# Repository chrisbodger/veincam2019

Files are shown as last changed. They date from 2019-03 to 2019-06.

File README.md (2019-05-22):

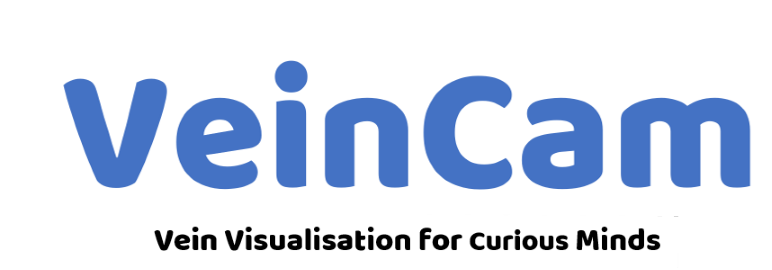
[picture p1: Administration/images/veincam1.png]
VeinCam


VeinCam is an educational tool for vein visualisation. It uses near infrared (nIR) light and a camera to stream a real-time image where veins can be easily seen. It is an open-source, build-it-yourself device so anyone who finds it useful will be able to construct it. There is a how-to guide of what materials to buy, how to put them together and the software to upload to get it all working.

This is the repository for the continuation of the VeinCam Project as an ANU Engineering Captone Project in 2019. The repository for the previous work can be found [HERE](https://www.github.com/chrisbodger/veincam). This repository will be used to delineate and document the progress made this semester, in what is to be the next chapter of this exciting project. 

---
# Table Of Contents
1. [Project Goals](#1-project-goals)
2. [Feedback](#2-feedback)
3. [Project Updates](#3-project-updates)
4. [Concept of Operations](#4-concept-of-operations)
5. [Meeting Minutes](#5-meeting-minutes)
6. [Decision Log](#6-decision-log)

---
# 1. Project Goals
There are 3 goals we wish to achieve this semester:

1. Develop a set of hardware requirements that are suitable for the VeinCam Project.
2. Optimise the software to run more efficiently.
3. Compile procurement options to develop kits to be able to be sold onto those who wish to build a VeinCam for themselves.

# 2. Feedback
A feedback form has been created for the interest of our stakeholders, should they wish to pass on any changes or improvements they believe to be prudent. The form can be found [here](https://goo.gl/forms/8cw5eWdaOY5C1jBo1).

# 3. Project Updates
### Week 11 - 22/05/2019

### Poster Showcase
The team presented VeinCam to a large science and engineering audience at the Project Showcase on the 20/5/19. A summary of the presentation and feedback is available [here](Administration/Communications/Poster-Presentation-Summary.md).

### School Visit
The team showcased VeinCam to Gungahlin College and gained insightful feedback into how VeinCam could be used in a secondary school environment. A summary of the visit is available [here](Administration/Communications/Gungahlin-College-Visit-210519.md).

#### Hardware
Final prototypes of the VeinCam enclosure completed, along with some PCB changes to better utilise onboard LEDs. Pricing for enclosure, along with final bill of materials determined. 

### Software

This week was spent getting all documenation up to date. Colour functionality added to MJPEG steam, fixed banding effects and scaling to better suit mobile and tablet users. 

### Previous Updates
More specific updates regarding each sub-team are available in the sub-team work diaries. These can be found in the [Hardware](/Hardware/HardwareDiary.md) and [Software](/Software/SoftwareDiary.md) folders, as well as team [Decision Logs](/Administration/Project/Decision-Log.md) are other locations for progress notes, should they not be located on this page.

# 4. Concept of Operations
Our Concept of Operations has been signed off by all parties involved. 

The [Concept of Operations](Administration/Project/CONOPS.md) document can be found in our repository.

# 5. Meeting Minutes
The team regularly meet to formally discuss the project's progress, as well as through other communication channels. the minutes from the formal discussions can be found in the [Meeting Minutes](Administration/meeting-minutes/) directory.

# 6. Decision Log
Major decisions that affect the majority or all of the project's future work and/or operations can be found in the [Decision Log](Administration/Project/Decision-Log.md/).

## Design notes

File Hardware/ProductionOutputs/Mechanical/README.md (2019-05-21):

## NOTE
We are relying on the draft angle from the laser cutter to hold the lens in. Different lasers/lenses/focal lengths will alter this draft angle and this needs to be taken into account.  

We also needed to flip the top acrylic to ensure that the lens would not fall out, as by default the lens was pushed in from the front. 

The dimensions may also need to be altered depending on how wide the laser cuts.

Any questions ask Josh, easier to explain with a VeinCam in hand and in person.

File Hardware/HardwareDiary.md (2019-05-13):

# Hardware Log

### Week Beginning 04/03/2019
* Looking into single board computers which would be suitable for the project.
	* Ideally smaller than a Raspberry Pi 3 B +, but more powerful than a RPi Zero.
	* RPi 3 A + was found as the only feaseable solution.
* Research into off the shelf cases which would suit above RPi 3 A + board, and required supporting hardware.

### Week Beginning 11/03/2019
* Rough design of possible case solutions, including extruded aluminium, COTS plastic enclosures, and custom cut acryllic.
	* Modeling of above designs in Fusion 360, including rough design of custom printed circuit assemblies to see mechanical fit.
* Preliminary schematic design for RPi 3A+ Hat to allow prelim BOM generation and costing.
* Preliminary schematic design for RPi Zero W Hat to allow prelim BOM generation and costing.
* BOM generation and component selection for both Hats.
* Estimated costing for both RPi Zero and RPi 3A+ devices, inclusive of PCA's and supporting hardware.

### Week Beginning 18/03/2019
* Created footprints and sourced / drew 3D models for all required components on PCA.
* Laid out RPiZero Hat, begun layout on RPi3A+ hat.
* Ordered parts from Mouser for new boards.
* Plans for RPi3A+ hat changed, no longer integrating charge circuit so changed schematic and laid out new design.
* Finished layout for both boards, got team approval, order placed 23/3/19 with JLCPCB. ETA Friday Week 5.

### Week Beginning 25/03/2019
* Extended discussions between Josh and Chris regarding possbile case designs going forward.
* Prelim case design for RPi3A+ completed. Awaiting boards for RPiZero before continuing with case design for the smaller platform. 
* General Makerspace + specific laser induction completed by Josh, will allow use of laser cutter to cut acrylic. 
* Shopping trip to purchase all required hardware for prototype build. 
* Test fitting and changes to mechanicals to account for differences in models vs actual.

### Week Beginning 1/04/2019
* Manufacturing of acrylic enclosure including updating lens mounting.
* Assembly of PCA's and testing, all appear to be functioning nominally. 

### Week Beginning 8/04/2019
* Laid out v2 of the VeinCam Zero to better fit a custom cut acrylic case instead of the official RPi case. 
* Begun design of v2 enclosure for the VeinCam Zero
* Changed VeinCam Plus enclosure to decrease size of IR acrylic required. 

### Week Beginning 15/04/2019
* Continued design of the v2 enclosure, and found it very hard to design around. 
* Through discussions with Ben and the team, have decided to scrap the zero due to the design challenges we will face wrt hardware, and the lack of performance which software is experiencing. 

### Week Beginning 22/04/2019
* Cut new case designs including IR acrylic for first time.
* Handed out to team members and Ben, awaiting feedback before continuing further. 
* DFM improvements to the VeinCam PCB

## Week Beginning 29/04/2019
* Resign of the enclosure to address issues with latest rev + shrink IR lens size. 

## Week Beginning 6/5/2019
* Laser cutting of revised case
* Assembly instructions written up

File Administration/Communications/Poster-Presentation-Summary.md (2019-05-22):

The Poster Presentation was held on the 20/5/19 in the Hannah Neumann building at ANU. VeinCam saw a strong number of people interested and participate in the presentation.
All members were present at various times during the presentation. Our stall had a VeinCam running to demonstrate on people's arms, a website on another touch-screen laptop for virtual representation and of course, our poster, which drew in the crowd and several people commented on its design and professionalism.
In particular, one university colleague of Alex stated that someone had come up to them and said they were "very impressed" with what the VeinCam team had achieved.

Matt from Questacon, a client for another Capstone project group, gave suggestions as to how VeinCam could potentially be upscaled to be made into an exhibit at the Q-Lab:
- A large high resolution camera with a large screen. The camera faces down, and patrons place their arm underneath.
- Signage could encourage blood flow in the way of exersice, such as 10 jumping jacks, to then see how that affects bloodflow in the arms.
- VeinCam kit could then be sold in the gift shop!
- A potential Capstone project for the following semester.

Other patrons pointed out to us that being a cheap, infrared camera, that it could be further developed to have several other uses:
- Night sight camera/cheap doorbell security option.
- Temperature/heat signatures at a low level (much cheaper than ones on the market currently).
- Assisting in household chores where detecting hot spots would be useful. 

Overall, the VeinCam team's presentation was a success and provided an engaging, interactive experience for its audience.

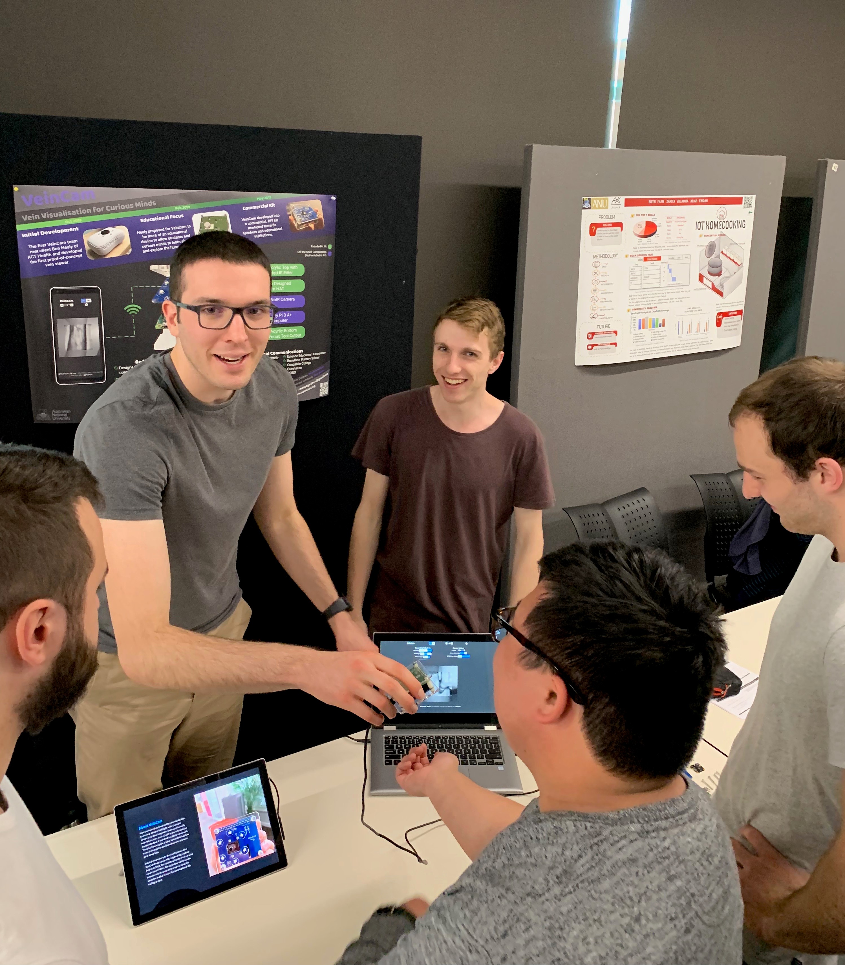
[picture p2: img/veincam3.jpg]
VeinCampres


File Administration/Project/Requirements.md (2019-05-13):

| Author        | Date Modified           | Version | Completion Status  |
| :-------------: |:-------------:| :-----:| :----:|
| Alexander Ollman   | 13/05/2019 | 2.0 | Completed for Audit 3 |

# System Requirements

| System Requirement  | Metric | Test | Validation | Client Importance (1 Lowest - 5 Highest) | Requirement Met? |
| :-------------: |:-------------:| :-------------:| :-------------: | :-----:| :----:|
| Compared to other devices with similar functionality, the produced device must be relatively inexpensive.  | Dollars, Australian | <$500AUD (Typical Public School Science Budget) | Cost of production VeinCam (minus packaging, freight, external costs) is less than $150 to consumer. | 3 | Yes, with reservation |
| The device must be simple to construct, easily reproduced (and/or easily manufacturable).  | Cost per unit | Cost per unit is <50% of total cost to consumer; contains mostly off-the-shelf components; can be manufactured with common machines, worldwide. | Cost per unit of is $13.49 for designed componentry, remainder of cost is from off-the-shelf components (Raspberry Pi A+, PiCam). Designs are open source and easily manufacutred with a laser cutter and PCB routing machine. | 5 | Yes, with reservation. |
| The device must be simple to use. Ease of use should be correlated with the intended educational application of the device, and as such be relevant for expected users. | Time, minutes | Time taken to assemble by unknown party, student. | Nursing student (Rachael Weigand) assembled VeinCam prototype closely resembling final design in 8 minutes (without camera focus adjustment, software setup). Device does not require further software setup and only knowing how to connect to a WiFi network is requied. | 2 | Yes, with reservation |
| The device must be able to use near infrared (NIR) illumination and real-time image processing to make veins appear most visible in an efficient manner. This criterion must be of a level of quality that is satisfactory for educational use. | #Infrared LED's | #Infrared LED's > 0, Veins Clearly Visible | There are six dual-wavelength (840nm and 950nm) infrared LED's which provide sufficient illumination on a subject and show clear, defined veins in the majority of test subjects (dependent on skin type, body fat) | 2 | Yes |
| The device must run primarily off of battery power. | Battery Capacity (mAh) | Battery Capacity > 0 mAh | The device contains no internal battery. However, the device is light and portable enough to be comfortably used with an external battery. | 1 | Yes, with reservation |
| The device must be able to wirelessly connect to an external device with a screen. | Wireless Connectivity Capability | - | Unit contains Built in WiFi + Bluetooth capability, connects to any external device with a screen and WiFi capability using WLAN connection | 4 | Yes |
| The device must be portable and mobile. | Weight, grams (g) | Total Net Weight < 200g | Unit is light (110g) and is easy and comfortable to hold in one hand. Device requires external power, which requires a cable connected to an external power source. This will commonly be either an exernal battery pack, a personal computer or an AC wall socket. | 4 | Yes, with reservation |
| The device must be reasonably easy to maintain, clean and fix in the event of failure/break/degradation. | Time, minutes | Time taken to be disassembled and reassembled by unknown party, student. | Device is completely modular and can be disassembled within 5 minutes, without the need for tools. Individual parts are easily accessible and two of the three major components are off-the-shelf. | 3 | Yes |
| The device should display veins in a wide variety of use-cases. | - | Veins clearly visible and defined on wide on differing external parties (e.g. dark-skinned, tattooed, hairy) | The device has not been tested outside of the testing confines of the project in accordance with ANU Ethics guidelines. Within our own testing, we have verified veins are clear and visible on a limited yet varied user sample size. | 5 | Untested, with reservation |
| The device is manufacturable with  the potential to be put to a commercial market. | Dollars, Australian | Complete Bill of Materials, including cost with potential for >100% markup. | The component designs, Bill of Materials, source of components and manufacturing costs of the device have validated that this is a commercialy manufacturable and viable product. VeinCam's marketability with be the responsibility of the client but has been discussed in the Commercial Viability document [here](https://github.com/chrisbodger/veincam2019/blob/master/Administration/Project/Commercial-Viability.md).  | 5 | Yes |

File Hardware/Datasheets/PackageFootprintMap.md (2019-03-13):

|Symbol|Package|
| --- | --- |
|SFH7254|PLCC-4|
|MCP73871|20 Pin 4x4mm QFN 0.5mm Pitch|
|TPS61092|16 Pin 4x4mm QFN 0.65mm Pitch|
|BSD235N|SOT-363|
|Switch|RR-12D07-VG|
|MMUN2133L|SOT-23|
|USB_B_MICRO|10118193|
|MCP3021|5 Pin SOT-23|
|10k NTC|0603|
|BATT Conn|JST-XH2 Right Angle THT|
|Inductor|Bourns SRN6045|
|100u Tant|D Case|

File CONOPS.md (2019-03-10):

# Concept of Operations

## Version History
| Version | Description |
| --- | --- |
| A | Initial Document |

## Table of Contents
* [Project Vision](#project-vision)
  * [Value Proposition](#value-proposition)
  * [Project Scope](#project-scope)
* [Stakeholders](#stakeholders)
  * [Project Team](#project-team)
  * [Project Client](#project-client)
  * [Shadow Team](#shadow-team)
  * [Course Tutor](#course-tutor)
  * [Course Convenor](#course-convenor)
  * [Users](#users)
* [Resources](#resources)
  * [Funding](#funding)
  * [Tools](#tools)
* [Project Management](#project-management)
  * [Deliverables](#deliverables)
  * [Milestones](#milestones)
  * [Audit Goals](#audit-goals)
  * [Timelines](#timelines)
  * [Work Breakdown Structure](#work-breakdown-structure)
  * [Decision Making and Conflict Resolution](#decision-making-and-conflict-resolution)
* [Risk Analysis](#risk-analysis)
  * [Safety Risk Analysis](#safety-risk-analysis)
* [References](#references)

---

## Project Vision
VeinCam is a device that enables the visualisation of the superficial vein system, and its purpose is to a tool to be utilised in the education of the human body and its functions. The device is based on the [Venenfinder project](https://hackaday.io/project/26158-assistance-system-for-vein-detection) submitted during the 2017 Hackaday event, and a prototype was developed in 2018 to extend the Venenfinder to become smaller, portable, and simple to build by young students and inquisitive minds while being affordable

This Semester, the vision is to produce a marketable kit that remains affordable and convenient to sell to educators for construction and development within a class environment.  

### Value Proposition
Our VeinCam device will help students better understand venous sites by augmenting visualisation of upper limb veins. It will provide students with a better understanding of venous sites around the body compared to an image or model.

### Project Scope
This project aims to continue on the achievements of the team from last semester and make the device marketable. This will include the optimization of the device and its software, including the option of migrating to a new hardware platform and rewriting some aspects of the program's code.

Continuing on from this, we will reach out to suppliers and manufacturers for the quote, order and manufacture of specialised parts. In doing so, we can have a complete bill of materials, costing and supplier sheet for the client to then use for the order to create the kits.

#### VeinCam Core Features
The VeinCam project utilises similar hardware to the Venenfinder project (Raspberry Pi, PiCam, IR LEDs) and extends the software's capabilities to automatically adjust the infrared light filtration, brightness and contrast to produce the clearest image possible with limited manual adjustment. The device is smaller than the Venenfinder despite being battery powered and completely wireless.

#### Future Marketing and Procurement Plans
The device will receive optimisations to ensure it is the best product possible before going to market. Simultaneously, procurement options will be explored.

Several avenues will be explored in efforts to optimise the device. this will include new hardware options for consideration, as well as software implementations that may lead to a software rewrite if necessary (changing from one language to another). These options will be discussed as a team going forward before agreeing on the final optimisations.

---

## Stakeholders
The following groups have been identified as stakeholders for this project:

| Stakeholder | Project Interaction |
| --- | --- |
| Project Team | Produces the Project Output and actions constructive feedback from other stakeholders |
| Project Client | Provides feedback on project progress |
| Shadow Team | Observes the Project and provides constructive feedback |
| Course Tutor | Provides feedback on project progress |
| Course Convenor | Provides feedback on project progress |

### Project Team
The project team consists of six undergraduate engineers who each have roles as point people in the project. All members of the team should be present to support each other in whatever way is necessary to complete tasks and better the project. The designated roles give each member a lead position, they are responsible for their sections and as such if any questions from external stakeholders specifically address a section of the project they are the member to contact.

| Name | Role | Email |
| --- | --- | --- |
| Christopher Bodger | Procurement and Research | u5395595@anu.edu.au |
| Alexander Ollman | Stakeholder Liaison | u5826805@anu.edu.au |
| Alexander Binos | Software Engineer | u5799782@anu.edu.au |
| Patrick Wilton | Software Engineer | u6050506@anu.edu.au |
| Josh Johnson | Hardware Engineer | u6044123@anu.edu.au |
| Tomas Johnson | Secretary | u6080168@anu.edu.au |

#### Responsibilities of the project team to the project
* Fulfil the tasks assigned by the team within the desired time frame to the best of their ability.
* Communicate the progress and setbacks of their tasks regularly with the team.
* Commit to regularly attending scheduled meetings, or otherwise remain up to date with meeting minutes and contributing to meeting agendas.

##### Responsibilities of the Hardware Engineer
* Manage and design the hardware of the device.
* Design and test the layout and chassis of the device.
* Manufacture of the prototype device.

##### Responsibilities of the Software Engineer
* Design the code for the device to meet deliverables and requirements.

##### Responsibilities of the Stakeholder Liaison
* Be the point of contact for general communication between stakeholders.
* Organise meetings with the client and other stakeholders when necessary.

##### Responsibilities of Procurement and Research
* Perform research required to strengthen the project.
* Obtain financial information regarding the manufacture of the device components.
* Delegate research when necessary to other team members.

##### Responsibilities of the Secretary
* Maintain the repository.
  * Including all documentation and meeting agendas/minutes.

**To reiterate these roles show who questions should be directed to and are not indicative of workload.**

### Project Client
Ben Healey (message2ben@gmail.com)

Ben is medical practitioner and an employee of ACT Health. He personally began this project using pointers from open source projects such as the 2017 Hackaday project and the Venenfinder project, to develop an affordable vein imaging device.

Due to Ben's increasing work commitments by ACT Health, both Chris Bodger and Alex Ollman will act as "Client by Proxy", due to their history with the project, and previous understanding of the project's desired direction.

#### Responsibilities of the project team to the client
* Design a device to meet the established baseline requirements that the client has presented.
* Inform the client regularly with updated progress towards milestones and any setbacks they should be aware of.

#### Responsibilities of the client to the project
* Provide information and requirements about the project to the team.
* Respond to communications on a regular basis.
* Be present and prepared at scheduled meetings.

### Shadow Team
ANU undergraduate engineering students, tasked with reviewing this project to provide an external viewpoint on the outputs and governance of the project. Shadow Team still to be formed

| Name | Email |
| --- | --- |
|  |  |
|  |  |
|  |  |
|  |  |
|  |  |
|  |  |

#### Responsibilities of the project team to the shadow team
* Provide shadows access to all information surrounding the project, including repositories, documentation and relevant communications.  This information should be up-to-date and presented appropriately.
* Be open to feedback from all channels from shadows, and act on feedback appropriately.

#### Responsibilities of the shadow team to the project
* Remain up-to-date with the activities, outputs and governance of the project through information that is supplied to them.
* Commit to providing constructive, accurate and actionable feedback to the project through the pathways provided to them: including formal audit feedback, as well as verbal feedback in tutorial sessions and through the feedback forms supplied.

### Course Tutor
Jenny Simmons (jenny.simmons@anu.edu.au)

ANU ENGN4221 course tutor for Semester 1 2019. Tasked with formally organising and directing weekly tutorial sessions where the project is planned, presented and reflected upon.

#### Responsibilities of the project team to the course tutor
* Provide the tutor access to all information surrounding the project, including repositories, documentation and relevant communications. This information should be up-to-date and presented appropriately.
* Be open to feedback from the tutor, and act on feedback from all channels appropriately.
* Be present and prepared at all weekly tutorials (Tuesday 10-12), appropriate to the activity of the tutorial that week.
* Be informed of the structure of the course and related assessment milestones as established by the course convenor.
* Be prepared to submit assessments, and be open to grades and discussion of grades with the course tutor.

#### Responsibilities of the course tutor to the project
* Be present and prepared to lead the tutorial each week, appropriate to the activity of the tutorial, and remain up-to-date with the progress of the project.
* To a reasonable extent, assist the project team with the progress of the project, including answering relevant and reasonable questions, and providing constructive, actionable and accurate feedback, particularly at times of project audits and during tutorial sessions.
* Reply to correspondence (email) in a timely fashion, and grade formal assignments fairly and appropriate to the quality of the project.

### Course Convenor
Chris Browne (chris.browne@anu.edu.au)

ANU ENGN4221 course convenor for Semester 1 2019. The course convenor is the overall authority and organiser for this course, and hence the projects that run through this course.

#### Responsibilities of the project team to the course convenor
* Same as those applying to the course tutor.

#### Responsibilities of the course convenor to the project
* Same as the course tutor with the addition of:
* Organise the course appropriate to the desired outcomes and be receptive to feedback regarding this structure. Information regarding the structure and assessment milestones of the course should be available to students within a reasonable timeframe.

### Users
Members of the public, particularly students and educators who wish to utilise the device for educational purposes.

#### Responsibilities of the project team to the users
* Provide members of the public access to information that pertains to all aspects of the project.
* Design a device that, at minimum, must not endanger the safety of potential users.
* To the best of their ability, provide the public with the information to design an affordable device that can image the veins of a person.

#### Responsibilities of the users to the project
* Members of the public have little steadfast responsibility to the project team.
* Ideally, members of the public will provide feedback on the function of the device during requirements analysis or testing.

---

## Resources
### Funding
Due to the researching nature of this project, there should be minimal costs for the projects. the only risk to this is the potential for the procurement of different hardware for testing, should it be deemed necessary by the team.

Regardless, a [Bill of Materials](#bill-of-materials) will be generated as these costs reveal themselves, and will be used to show what the procurement and research team member has arranged for component pricing with suppliers. Costing will be updated as this information comes to light.

### Tools

with the potential to continue development with componentry, the tools likely to be used throughout this project include:
- Soldering Iron
- 3D Printer
- Laser Cutter
- Dremel
- Screwdriver, screws, nuts and bolts.

All safety precautions outlined by the ANU Makerspace's Terms and Conditions will be followed during the use of instrument or tool, regardless of where and how it is used. A safety risk analysis has been performed at the bottom of this document.

#### Project Administration
* GitHub
* Google Drive
* Discord Communications Platform

#### Manufacturing and Testing
* Ian Ross Design Studio
* ANU Makerspace

##### Bill of Materials
An initial Bill of Materials has been drafted below of what we expect the project to cost.

| Component | Cost (AUD) | Supplied By Client |
| --- | :---: | :---: |
| | | |
| | | |

Please note that component pricing is not finalised and is suitable for a quotation only. Manufacturing costs can vary with the price of raw materials as determined by the suppliers.

#### Programming
Source code from the last semester of development will be modified for the optimisation of the current platform, or rewritten if deemed appropriate. A snapshot of the code has been captured and archived within the [repository](/master/Software/Initial%20Code).

**FEATURES INCLUDE**
---

## Project Management
### Deliverables
The initial deliverables are as follows:

#### Baseline Deliverables
* Determine the suitability of the current hardware and if it should be replaced with a more appropriate platform.
* Optimise the software for the desired hardware to run more efficiently, as outlined in the [Requirements](NEED LINK HERE) document.
* Compile a list of procurement options and outline sources for the client to then purchase and build the kit for distribution.

**DECIDE OF STRETCH GOALS**
#### Stretch Deliverables
In order of priority.
* Implement manual controls for image adjustment.
* Compile user feedback on the construction and use of the device (based on the written guides).
* Optimise for different use-case scenarios (e.g. tattooed skin, dark skin).
* Design or source an appropriate hands free stand to mount the device.
* Optimise device to visualise blood flow to identify best candidate vein

#### Ultra-Stretch Deliverables or Future Project Aims
* Configure device to run off of Pi Zero module
  * Offload image processing to secondary device

### Milestones
Further detail on the optimisation of milestones and design aims of the prototype are detailed in the Requirements document.

#### Milestone 1
Decide on final hardware appropriate for the project's vision

#### Milestone 2
Optimise software to run as efficiently as possible for the desired platform

#### Milestone 3
Compile quotations for external manufacture of components (PCBs, case, etc.)

#### Milestone 4
A kit of compiled components ready for distribution.

### Audit Goals
#### Audit 1
* Complete ConOps Version 1
* Reach Milestone 1

#### Audit 2
* Update ConOps to Version 2
* Complete requirements analysis
* Reach Milestone 2

#### Audit 3
* Achieve Milestone 3/4 with accompanying verification and validation

Milestones are subject to change as the project evolves.

### Timelines
An [indicative schedule](https://docs.google.com/spreadsheets/d/1nfNqFCF2ieP5CyVmqDSeZ3oXegxcCG4hojdd6fMcq9Y/edit?usp=sharing) has been drafted for the project.

**REWRITE THIS**
### Work Breakdown Structure
1. Requirements Analysis
   1.1. Review PoC
   1.2. Perform risk analysis
   1.3. Brainstorm requirements (in-house)
   1.4. Develop requirements with client
   1.5. Finalise requirements
2. Prototyping
   2.1. Design hardware
   2.2. Manufacture and construct hardware
   2.3. Design baseline software
   2.4. Integrate software
   2.5. Update software with stretch deliverables
3. Validation & Verification
   3.1. Test prototype in-house
   3.2. Conduct performance review
4. Documentation
   4.1. Write ConOps v1
   4.2. Update ConOps v2
   4.3. Create "How-to" guide
   4.4. Create poster
   4.5. Organise repository

### Decision Making and Conflict Resolution
Decision making will be by consensus in consultation with the client. When consensus cannot be reached the project team will seek advice from other stakeholders depending on the nature of the decision. For further detail please refer to the [Decision Log](/docs/Decision-Log.md).

---

**REWRITE THIS**
## Risk Analysis
All risk analysis performed throughout this project will be in accordance to the Australian and New Zealand Industry Standard AS/NZS 4360:2004.

Risk Matrix

Potential risks to the success of the project have been brainstormed in order to understand them and mitigate either their severity or likelihood.

| Risk | Consequences | Likelihood | Severity | Mitigation |
| :---: | :---: | :---: | :---: | :---: |
| Not clearly understanding or defining client's requirements for the project. | Product does not meet client requirements, client dissatisfied, requires re-doing work, going over budget and schedule to redesign | D | 3 | Maintain regular contact with client regarding progress and milestone completion. |
| Not defining scope of project and setting clear and achievable milestones. | No clear definition of project progress, feature creep over time results in lack of physical product, no clear "stopping point" for project or completed product, client dissatisifed, product does not meet customer requirements, likely to be over-budget. | C | 3 | Defining scope early and ensuring we stick to milestones and their respective outputs to ensure we do not deviate on a project tangent. |
| Device cannot be utilized as a medical device due to not meeting medical certification criteria. | Unable to deliver product to medical professionals, which is client's ultimate goal for the project. | C | 2 | Ensure client is aware of potential certification issues, and that they verify during development whether the device can be used with and/or without the medical classification. |

### Safety Risk Analysis
In developing the prototype there is a chance of injury, similar to above these risks have been listed and steps taken to mitigate their severity or likelihood.

| Risk | Consequences | Likelihood | Severity | Mitigation |
| :---: | :---: | :---: | :---: | :---: |
| Personal harm whilst using listed tools (incl. burns, shocks, cuts) | Pain, discomfort and possible medical attention. | D | 3 | Ensuring all team members are familiar with the safety training of the ANU Makerspace/Engineering workshop, supervision by one other team member when using potentially dangerous tools. |
| Damage to Hardware due to physical impact or electrostatic discharge (ESD) | Loss of data, hardware faliure, schedule delays to order and replace damaged hardware. | E | 4 | Ensuring hardware is never placed in an area where it is likely to be damaged, always in full visible sight. Observing proper ESD safety techniques, such as regularly grounding ourselves and only contacting circuitry by edges. |

---

## References
[Venenfinder Github](https://github.com/Myrijam/Venenfinder)

[Venenfinder Hackaday.io Page](https://hackaday.io/project/26158-assistance-system-for-vein-detection)

---

This Project is licensed under the Creative Commons license.

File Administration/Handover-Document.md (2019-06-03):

# Handover Document

This document is intended for the use of the Primary Client Ben Healy, for future project teams who are continuing with this project in future semesters. This document summarizes the development and progress of the project summarised as of November 2018.

## 1. Aims and purpose of this project
This project was started by the client who wished to develop an accessible and low-cost device that could be developed for the public for the purpose of enhanced vein visualisation using infra-red light - the VeinCam.

The client was delivered a preliminary prototype of the VeinCam at the end of the second semester in 2018
A full list of the project goals and stretch goals are in the [Concept of Operations document (ConOps)](/docs/CONOPS.md).

The project team is a group of four undergraduate ANU Engineering Students who completed a course which involved development of something as per the requirements and directions of the client. The course began in July 2018 and completed in November 2018.
A full list of the relevant stakeholders and their responsibilities at this stage of the project are
in the[ConOps](/docs/CONOPS.md).

The requirements developed by the project team and agreed upon by the client are listed in detail in the [Requirements](/docs/REQUIREMENTS.md)

## 2. Key development milestones and decisions
Key decisions are summarised only in this document, with full dates, relevant teams involved and justifications in the [Decision Log](/Administration/Project/Decision-Log.md)

Main milestones in Software and Hardware development are summarised below. For more details, visit their respective work diaries:
[Software Work Diary](/Software/SoftwareDiary.md)
[Hardware Work Diary](/Hardware/Team-Work-Diary.md)

### 2.1. Software Development
####Increased Frame Rate and Functionality
At the beginning of the semester much of the code was taken from open-source resources without many changes; and although this provided a good initial proof of concept of what the VeinCam was capable of. Considering the commercialisation goals for this semester it was important to evaluate what areas the team needed to improve upon for VeinCam to become a viable product. The most obvious of these was the frame rate of the device which at the start of the project was sitting on a max of around 3 FPS. This was fixed by changing to MJPEG recording and splitting the frames within the bytes stream (now 20-30 FPS). After the code had been cleaned (described below) other functionality including the following was added to increase VeinCam's clean aesthetic and list of features:
* The ability to use continuous image capture (YUV - the old method) for very slightly better image quality for taking still image screenshots
* Colour functionality (This only works without the IR filter of course and reduces the frame rate to around 8 FPS), under many lighting conditions this can make the veins stand out quite a bit (Dark Blue colour)
* Dynamic scaling (to a max value) of the image on the web page UI and fixed unnecessary scrolling
* Boot LED will come on after the pi has finished its normal boot process for a better indication of process
* Ready LED will come on once app.py has finished its imports and the server is running
* Camera can now be turned on and off quickly on the server side without causing the app to crash
    * Many other small bug fixes that would cause the script to raise an error under certain conditions

####Code Readability and Room for Extra Features
Following on from improving the frame rate and gathering an understanding of how each of the components of the code worked together, the team wanted to make the code more readable, reduce its complexity and inherently make it more original and flexible so that it could be used better as an open source project for others to expand upon. The two scripts dedicated to the camera functionality and image processing were merged into one with an easy to read three class structure including one class specifically for the new MJPEG stream output. The altering functions within app.py were all merged into one and generally both scripts needed many redundancies removed, variable name changes and other syntax fixes for consistency across the code.

####Potential Improvements
Currently many things could be improved in software for extra functionality. The UI is in very usable state, but could still be more dynamic and better designed for use with mobile devices and very large computer screens (such as projectors). It may be worth looking into building much of what is there from scratch rather than taking almost every HTML class from large css libraries. The possibility of creating a binary image of the veins was investigated though due to the power of raspberry pi, this tended to reduce the frame rate too much, just global or adaptive thresholding alone would put the frame rate down to around 5 FPS on average let alone if you wanted to then perform eroding and dilating. Though it would be good to at least have this option because it can look quite good as a concept. Smart ways of increasing the resolution or even the focus in software could be very useful, as they seemed to be largest part of negative feedback after frame rate from the original design. The raspberry pi's resolution is tied to its field of view so for this project it was decided to first focus on other things.

### 2.2. Hardware Development
####Low cost, easy to assemble enclosure   
Last semester, the previous team had a 3d printed enclosure that was perfect for a prototype, however would not be appropiate for mass manufacturing. As the goal for this semester was to get the product ready for commercialisation, the enclosure was redesigned to allow for production in quantity at a low unit cost, along with being cheap and easy to ship and assemble. This resulted in a laser cut acrylic case which is held together with screws, which is both cheap and easy to manufacture and ship, but can also be assembled easily with a phillips head screwdriver.   

####Design of a highly integrated printed circuit board  
Moving to production hardware required a printed circuit board to hold the IR array, status LEDs, and the NoIR camera. This board played a key role in both the electrical and mechanical design, as on the electrical side it enabled a low cost and easily manufacturable way to connect all of the electronic components, whilst also allowing for the NoIR camera to be mounted in a low profile manner. 

####Potential Improvements
There is still room for improvement in the mechanical design, as whilst the method of holding the IR lens in place is functional, it is not exactly elegant.   
Currently the VeinCam also requires an external battery pack, which adds extra volume and makes it harder to hold onto. Whilst a version of the VeinCam with an integrated battery was partially designed, it was abandoned due to the added complexity of a fully integrated solution. An area for improvement may be taking a middle ground through figuring out a way to mount an external battery pack to the VeinCam, which will make it into one unit whilst not having the complexity and cost of a fully integrated solution.

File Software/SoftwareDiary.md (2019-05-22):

# Software Log

### Week Beginning 04/03/2019
* Took time to understand the previous code at a high level with help from previous team members
    * Resulted in the creation of a Visio diagram to visualize the overall system and what files were being used in what order.
    * Used the existing functioning RPi Zero to understand the limitations it currently has and how it performed under different conditions
* Ensured screen capture capabilities were working for virtual meetings for later code visualisation

### Week Beginning 11/03/2019
* Identified areas of optimisation and improvement including:
    * Further image processing to better identify the veins
    * Optimisation of boot time and better indication to user of the boot progress
    * Improving front-end web page including more options, functionality, usability and information
    * General code cleaning and optimisation
* Static image processing testing was set up for quick idea verification using MATLAB given its inbuilt image processing capabilities
* Steps were taken towards getting the existing code's 'development' mode working on a windows machine for easy testing using the Flask server

### Week Beginning 18/03/2019
* Officially got development server working on multiple Windows 10 systems
    * Using this the cropping and histogram image regions were adjusted for better testing
    * Variables such as frame rate and histogram equalisation values were generalised for easier testing as well
* Brainstorming took place discussing how a new front end might look and whether a small loading screen would be beneficial
    * An example loading gif was made with external help to be implemented later on

### Week Beginning 25/03/2019
* Initial VeinCam software was tested on the newly acquired hardware
    * Existing software proved to work on both the Pi A+, B+ and Zero W models
* Begun testing the software for bottlenecks: mainly looking for boot time and frame rate issues
    * Image processing confirmed not to be a problem through testing on camera_piopencv
        * Also investigated image resolution, array storage, pi gpu memory, server refresh rate, 
        camera video capabilities, and frame rate manipulation on the development server.
    * Looks as though the python script speed is not the cause of poor frame rate.
    * CPU capabilities were ruled out as cause of poor frame rate
    * More investigation needs to be done to find the root cause of poor frame rate
    
### Week Beginning 01/04/2019
* Cause of poor frame rate was found to be method of capturing images for processing as pi camera has small amount
of inbuilt post processing on captured images in specific formats
* Changed to a MJPEG stream and captured images via splitting bytes string.
    * Was followed up by decoding to a row vector and converting to a grey scale image
    * This did lose a small amount of image quality and hence will investigate how we can improve this
    * Initial tests indicate that now the pi A+ is capable of 30 FPS and the Zero W ~5-10 FPS
* Code was changed so that LEDs were mapped to correct pins on new prototype VeinCam/Plus hardware
* Code was improved slightly for readability, much more will be done on this now that frame rate is fixed
    * New code will be uploaded once this to a reasonable standard as at the moment code has had to be changed almost
    entirely via nano text editor so this is a slow process, even with local SSH capabilities
* Development started to better indicate boot progress with new boot and status LEDs. Will continue into next week.

### Week Beginning 08/04/2019
* Boot LED now writes directly after Pi finishes normal boot process
    * This gives a better indication of boot progress, talk of using hardware to put this light on from actual boot (using negative logic)
    * General syntax fixes were made to camera_emulated code
* General testing of current revision of code was done to test camera under different lighting conditions
    * Linear artifacts were noticed most likely due to MJPEG stream
    
## Week Beginning 15/04/2019
* Planning for how code would be cleaned (mainly converging camera_piopencv and camera_base) including defining each function and how they interact with eachother
* Plans for how software will move forward were set
    * It is difficult to say whether Image quality can be further improved
        * This is due to the capabilities of the pi. Resolution is tied to Field of View
        * Almost no image processing is done and even with image processing off, frame rate and quality does not improve
        * Changes to camera settings such as sharpness, gain, etc. do not make the image more clear especially in temrms of veins and can slightly reduce framerate.
* Plans to make a code document for how each function works for educational tools and handover will be made once cleanup has commenced

## Week Beginning 22/04/19
* Code for camera_piopencv and camera_base was significantly changed to now be in one file with only three classes
    * Readability was improved, many code redundancies were found and removed, and many other minor variable name changes and syntax fixes were changed for user readability
* Small amount of commenting was added, and references to open source code were kept where necessary.
* Small hardware faults and changes were pointed out and fixed or revised for further board spins including:
    * IR LEDs being the on the opposite pins to what they were on original schematics
        * This was changed in software and subsequently changed on the schematic
    * SD card is still too difficult to remove, although it was brought up whether we want to be able to remove it at all depending age group client wants to most target
        * Notch in current acrylic will be made slightly wider
    * HDMI port on the A+ gets a little too hot after prolonged use of having the camera on (maybe 10 minutes)
        * This will be brought up with the client as future iterations of the project may want to go to a fully enclosed design
        * For the moment, the acrylic was made slightly wider on all sides
        
## Week Beginning 29/04/2019
* Plans of how app.py will be cleaned and made more readable
* Feedback from client of current software (outputs not actual code) were acted upon where necessary
    * Meeting will be set up as to where the software needs to go within the next three weeks
    * In the meantime app.py will be cleaned, software documentation will be written (including how each function works with new Visio diagram)
        * This will hopefully be included in current front end soon
* Some other members will now move on to helping with front end ideas implementation
    * First priority is getting loading GIF working, and making current front end mobile friendly especially with the video output
    
## Week Beginning 06/05/19
* Code was written to have both implementations of image capture available within the same script
    * This was done to increase options as sometimes the user may not care at all about the frame rate (3 FPS for image capture), seeing as this does provide very slightly better image quality
    * This was tested via manually changing a new settings cache value named 'state'
* Research was done into how we can dynamically change the size of the image so it looks good on phones and tablets, but still have limit so it wont become too big on pcs running the window in fullscreen
* Small app.py cleanup took place, mostly removing now redundant code and general syntax fixes

## Week Beginning 13/05/19
* Front End was changed so that the image capture technique can now be changed from server without the need to manually change settings file
* Largest concern from client was the linear artifacts present under many lighting conditions using the MJPEG stream
    * Initial testing indicated indicated that the most likely cause of these were the IR LEDs and how their refresh rate interact with the camera's frame rate
    * After a few calculations a new LED refresh rate value was found that was an integer multiple of the camera's frame rate (750Hz) (camera frame rate = 30Hz)
    * Implementing saw the linear artifacts almost completely disappear
* For added functionality the ability to change between colour capture (image is converted to LAB space and histogram equalisation is applied only to 'L' channel) was added both to the python side and server side
    * This drastically reduces the framerate (to about 6-8 FPS) though under certain lighting conditions this makes the veins easier to identify
    * Note that the camera will need to be reset if a user attempts to select YUV and Colour at the same time in a certain order
        * Plans were made to fix this in the future
* Server side scrolling issues were fixed so no scrollbar exists unless it is needed
* UI scaling of the image is now fixed so the image has a maximum size and also scales to 90% the width and height of its window if it is under this maximum.
    *This now allows the device to be used with mobile and tablet devices as intended
* Structure was laid out for code/software documentation (at this stage it will just be for future groups of VeinCam and the client himself)
    * If time allows for it, this will be turned into a educational resource as well with consultation from education professionals
    
## Week Beginning 20/05/19
* General app.py cleanup for readability and removing any redundancies
* Created Software README for functionality descriptions
* Updated Handover Document with major updates done over course of project and any other necessary information

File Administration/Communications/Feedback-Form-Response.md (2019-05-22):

Following our Poster Presentation, we recieved a message through our feedback form from an audience member who wishes to aid with the project in future!

**Have you got any feedback regarding the progress of the project so far?**

Very proud, though would recommend making the camera stronger as it would be useful in hospitals, on site at accidents (e.g. car) to look for any internal bleeding for example.

**Have you got any feedback or advice regarding the software and hardware development?**

Increasing the power of the rays, modifying the infra-red camera to more of an x-ray or even black-light to get through the layers of fat and really define the veins - designing the camera lens to have multiple layers upon one another. It is really hard to describe this so please contact me and I can explain further: cjvlat58@gmail.com

**Have you got any feedback regarding our communication, both internally within the project team or externally to our stakeholders?**

Great, loved the presentation, was engaging and fun. Couldn't fault it.

**Have you any additional feedback or comments for the project team?**

I have had several years of experience within robotics and though I may not be studying engineering or be enrolled at ANU, I would love to be able to look at the veincam and it's blueprints and maybe lend a hand towards it's improvement.
cjvlat58@gmail.com

This feedback has been passed onto the client.

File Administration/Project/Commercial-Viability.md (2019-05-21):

# Commercial Viability 

For a product to be commercially viable there are a number of key considerations which need to be taken into account. This document will cover a number of considerations which are relevant to the VeinCam project. 

### Manufacturing  
The first part of ensuring that VeinCam is a commercial success is making sure that it can be manufactured in volume at a reasonable price. Some of the key considerations to ensure this are listed below.  

- Utilising proven manufacturing techniques such as laser cutting and two layer printed circuit boards lowers the risk of the product not being able to be fabricated / fabricated at a reasonable cost. 
- Reducing the part count (both electrical and mechanical) has benefits from both a cost and complexity standpoint. This has occurred with VeinCam, as the part count has been reduced during the prototyping stages to a point where is cannot be reduced further whilst keeping the current feature set. One such example of this is integrating the camera adjustment tool into the bottom acrylic plate, as otherwise a separate tool would need to be shipped which adds complexity and cost.    
- Ensuring that the design of the printed circuit assembly has taken into account design for manufacturing and assembly requirements lowers the risk of the board failing fabrication and assembly. Specifically, using wide traces (10 mil) and large vias (0.6/0.3mm) ensures that any board house can manufacture the board as old process technology can be used. 
- Furthermore, using large components (0603), along with laying out the board with DFM considerations in mind ensures that the assembly process will have a high yield. This results from layout decisions which prevent tombstoning of components during reflow, and sufficent spacing of components from the edge of the board to prevent stress failures during depanelising. 

### Durability
Once the product is assembled, we need to ensure that it will stand up to the use and abuse which can be expected of a consumer electronics product. This primarily involves ensuring that material selection and assembly methods are sufficiently durable.   

- Utilising acrylic as the external enclosure ensures that it is strong enough to withstand scratching, dropping, and other forms of physical damage. Furthermore, the mechanical properties of acrylic do not degrade over the expected lifecycle of the product, and as such it can be expected that the VeinCam will be able to withstand these the above mentioned damage for its whole lifecycle. 
- Another important consideration is the durability of the PCB. Whilst the PCBA contains primarily surface mount components due to their smaller size and lower assembly cost, the Raspberry Pi connector has been chosen as a through hole part as it provides much greater mechanical strength which is required for a large connector of its type which can be expected to be inserted and removed a considerable number of times in its lifespan. 
- The mechanical assembly of the device, in using metal bolts to secure both the camera to the PCBA, and to hold the whole device together ensure that once assembled, the VeinCam will not be falling apart due to the front and rear panels not being attached to each other.
- Due to the design of the lens and the way it mounts to the front panel ensures that it is unable to fall out post assembly, due to both parts having draft angles which when assembled prevent the lens to move through the front of the front acrylic, and the camera being mounted flush behind the lens prevents it from falling out backwards. 
- The likelihood of electronic failure of the device is also quite low, as the Raspberry Pi and NoIR camera are both known as to be reliable products, and due to the good design considerations and trivial nature of the VeinCam board the likelihood of it failing is quite low. 
- The most likely failure methods of the device are damage to the flat flex cable during assembly, which can be mitigated through showing the best method to assemble it in the assembly instructions, and water damage, which could be mitigated through making a water resistant enclosure, however this would increase the physical size and cost of the VeinCam and as such it was decided against. 

### Safety

Is is obvious that if a product is to be commercially viable, is must be safe for the user to use. Outlined below are a few of the safety concerns we have considered in the development of the VeinCam. 

- One safety concern is the likelihood of any sharp edges cutting the user, small parts being able to be swallowed, or other forms of contact damage to the user. This has been mitigated through radiusing every corner on the device and insetting the SD card from the edge of the enclosure such that it can not be accidentally removed. 
- Amongst its other uses, the bottom acrylic plate serves as a way to protect the user from scraping their fingers across the numerous sharp pins sticking out of the Raspberry Pi, whilst also proving a way of holding the device which prevents the user from sticking their fingers into the sandwich of circuit boards. 
- If the user did somehow manage to stick their fingers into the printed circuit assemblies, the highest voltage on the board is 5 VDC, which falls into the 'extremely low voltage' IEC voltage range and is not considered hazardous. See [AS/ACIF S009:2006, Page 18](https://www.commsalliance.com.au/__data/assets/pdf_file/0009/2421/S009_2006r.pdf) for more information.
- The safety of the users images also needs to be considered, as if they were comprised it could lead to a number of issues. Due to the streaming nature of the device, images are not stored anywhere and as such cannot be easily stolen by an adversary. The easiest attack vector to gain images from the device would to be log into a currently streaming VeinCam and record the images displayed, however this would require the adversary to know the WiFi password of the VeinCam, and for them to be in close proximity of the device to be able to access the broadcast WiFi network.   

### Sourcing
Sourcing of the components also needs to be taken into consideration, as failure to source any given component of the VeinCam would prevent use and sale of the device. 
- All parts excluding the Raspberry Pi, NoIR camera, and the IR LEDs can be sourced from multiple suppliers at ease and are not a sourcing risk. Whilst the Raspberry Pi and NoIR camera are only available from a single source, they are mass produced items with high stock availability and is only a slightly higher risk item.  
- The high power IR LEDs on the other hand are only available from one supplier, and there are no other similar components available on the market. At the time of writing there are only 6700 LEDs available globally, and any quantities higher than that have a 5 month lead time. Fortunately only 6000 LEDs are required for a 1000 unit production run, and as such even accounting for overages there is enough supply to satisfy the VeinCams needs. However this could change at any point in time and as such it is an item which has a high risk of causing production delays if there is insufficient supply to meet the production demands.

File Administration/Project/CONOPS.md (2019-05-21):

# Concept of Operations

## Version History
| Version | Description | Audit Version |
| --- | --- | --- |
| 3.0 | Final Document | Audit 3 |

## Table of Contents
* [Project Vision](#project-vision)
  * [Value Proposition](#value-proposition)
  * [Project Scope](#project-scope)
  * [Project Comparison](#project-comparison)
* [Stakeholders](#stakeholders)
  * [Project Team](#project-team)
  * [Project Client](#project-client)
  * [Shadow Team](#shadow-team)
  * [Course Tutor](#course-tutor)
  * [Course Convenor](#course-convenor)
  * [Users](#users)
* [Resources](#resources)
  * [Tools](#tools)
* [Project Management](#project-management)
  * [Deliverables](#deliverables)
  * [Milestones](#milestones)
  * [Audit Goals](#audit-goals)
  * [Work Breakdown Structure](#work-breakdown-structure)
  * [Decision Making and Conflict Resolution](#decision-making-and-conflict-resolution)
* [Risk Analysis](#risk-analysis)
  * [Safety Risk Analysis](#safety-risk-analysis)
* [References](#references)

---

## Project Vision
VeinCam is a device that enables the visualisation of the superficial veinous system. It's primary purpose is to educate curious minds on the inner workings of the human body. The current VeinCam iteration, submitted as a ANU Engineering Capstone Project in late 2018, is based on the 2017 [Venenfinder Hackaday project](https://hackaday.io/project/26158-assistance-system-for-vein-detection). The objective of the VeinCam project was to extend the Venenfinder to become smaller, portable, more afforable and easy to build by young students and inquisitive minds.

After recieving incredibly positive feedback during the final presentation of VeinCam, from both educational and medical professional's alike, the decision was made to continue the VeinCam project into 2019. The vision for this next phase of development is to produce a Bill of Materials and finalised software to handover to the primary client. The quality of the Bill of Materials and software should be of a standard where the primary client can create commercially-viable DIY kits that remains affordable and convenient to market to educators, for construction and development within a classroom environment. As such, our goal of this project is to create a product that is professional and of a commercial standard.  

### Value Proposition
Our VeinCam device will help students better understand the human body by augmenting visualisation of upper limb veins. It will provide students with an interactive expereience and fun way to learn about the venous sites of the body. At an educational level, this has never been done before as commerically available products with similar capabilites are far beyond a price point that would be considered by educators. Our value proposition is to provide this experience and funcionality at a fraction of the cost. 

### Project Scope
This project aims to continue on the achievements of the team from last semester with the aim of polishing the device so that it is of a standard where it can marketable. This will include the optimization of the device's physical hardware and extending its software capabilities. To achieve this, we will explore the options of migrating to a new hardware platform and rewriting aspects of the current image processing code. 

The VeinCam will be designed and refined over several iterations, comparing off-the-shelf and custom made components using quotes from online stores and potential chassis manufacturers. The primary goal of this project is to supply the client with a complete bill of materials, costing and supplier sheet to then use for the order and manufacturing of educational kits.

Whilst two chassis, VeinCam (based on the Raspberry Pi Zero platform) and VeinCam Plus (based off the Raspberry Pi A+), were within the initial scope of this project, it was determined that a smaller VeinCam on the Pi Zero was redundant, as it was not cost-effective nor was powerful for our intended purposes. 

### Product Comparison
The following table contains an overview of how the newer VeinCam will differentiate from the current iteration.

#### Feature Summary
| Current VeinCam Prototype (v2.3)| VeinCam 2019 | Future Development/Stretch Goals |
| :---: | :---: | :---: |
| Raspberry Pi 3 B+ | Raspberry Pi A+ |  |
| IR Illumination (840nm) | IR Illumination (840-940nm, adjustable) | |
| Basic LED Array | Custom LED PCB | |
| IR PiCamera | IR PiCamera |  |
| HTML/CSS User Interface | JavaScript User Interface | Smartphone App Development |
| Startup Time < 1 min | Startup Time < 30 seconds | |
| Wireless, Portable and Battery Powered | Wireless, Portable, optional battery  | |
| Large 3D Printed Enclousre | Smaller Off-The-Shelf/Custom Design Enclosure(s) | |
| Manual Camera Setting (Brightness, Contrast etc.) Adjustment | Automatic Camera Setting Adjustment and Framing | |
| Basic Image Processing | Vision-Based Image Processing | Vein Object Detection |
| Open Source | Polished, Manufacturable Design | Commercial Educational Kit  |

#### VeinCam v2.3 Features
Currently, the VeinCam utilises similar hardware to the Venenfinder project (Raspberry Pi, PiCam, IR LEDs) and extends the software's capabilities to perform a histogram equalisation to allow veins to come through the image clear and prominent. VeinCam also features a web interface which allows for the manual adjustment of the camera's brightness, contrast and saturation to produce the clearest image possible. Unlike other open-source and commercially available vein cameras, VeinCam is smaller, battery powered and completely wireless.

#### VeinCam 2019 Core Features
- Smaller, more polished chassis using either off the shelf components for easy manufacturing of kit, or custom manufactured casing.
- Image Processing with more aggressive equalization, automatic image pixel brightness adjustment to differentiate and illuminate the arm from the background, vein detection and optimization.

---

## Stakeholders
The following groups have been identified as stakeholders for this project:

| Stakeholder | Project Interaction |
| --- | --- |
| Project Team | Produces the Project Output and actions constructive feedback from other stakeholders. Provides regular updates to stakeholders regarding process through the repository documentation and verbal communication |
| Project Client | Provides feedback on project progress and guides towards milestone objectives |
| Shadow Team | Observes the Project and provides constructive feedback |
| Course Tutor | Provides feedback on project progress |
| Course Convenor | Provides feedback on project progress |

### Project Team
The project team consists of six undergraduate engineers who each have roles as point people in the project. All members of the team should be present to support each other in whatever way is necessary to complete tasks and better the project. The designated roles give each member a lead position, they are responsible for their sections and as such if any questions from external stakeholders specifically address a section of the project they are the member to contact.

| Name | Role | Email |
| --- | --- | --- |
| Christopher Bodger | Procurement and Research | u5395595@anu.edu.au |
| Alexander Ollman | Stakeholder Liaison and Operations | u5826805@anu.edu.au |
| Alexander Binos | Software Engineer | u5799782@anu.edu.au |
| Patrick Wilton | Software Engineer | u6050506@anu.edu.au |
| Josh Johnson | Hardware Engineer | u6044123@anu.edu.au |
| Tomas Johnson | Secretary | u6080168@anu.edu.au |

#### Responsibilities of the project team to the project
* Fulfil the tasks assigned by the team within the desired time frame to the best of their ability.
* Communicate the progress and setbacks of their tasks regularly with the team.
* Commit to regularly attending scheduled meetings, or otherwise remain up to date with meeting minutes and contributing to meeting agendas.

##### Responsibilities of the Hardware Engineer
* Manage and design the hardware of the device.
* Design and test the layout and chassis of the device.
* Manufacture of the prototype device.

##### Responsibilities of the Software Engineer
* Design the code for the device to meet deliverables and requirements.
* Ensure the code is stable and respositories are up-to-date.

##### Responsibilities of the Stakeholder Liaison and Operations
* Be the point of contact for general communication between stakeholders.
* Organise meetings with the client and other stakeholders when necessary.
* Regularly update major documents when project deviates from documentation.
* Set and lead meetings.
* Manage the team and ensure goals and milestones are being achieved.

##### Responsibilities of Procurement and Research
* Perform research required to strengthen the project.
* Obtain financial information regarding the manufacture of the device components.
* Delegate research when necessary to other team members.

##### Responsibilities of the Secretary
* Maintain the repository, including all documentation and meeting agendas/minutes.

**These roles show who questions should be directed to and are not indicative of workload.**

### Project Client
Ben Healey (message2ben@gmail.com)

Ben is medical practitioner and an employee of ACT Health. He personally began this project using pointers from open source projects such as the 2017 Hackaday project and the Venenfinder project, to develop an affordable vein imaging device.

Due to Ben's increasing work commitments, both Chris Bodger and Alex Ollman will act as "Client by Proxy", due to their history with the project, and previous understanding of the project current progress and Ben's desired outcomes.

#### Responsibilities of the project team to the client
* Design a device to meet the established baseline requirements that the client has presented.
* Inform the client regularly with updated progress towards milestones and any setbacks they should be aware of.

#### Responsibilities of the client to the project
* Provide information and requirements about the project to the team.
* Respond to communications on a regular basis.
* Be present and prepared at scheduled meetings.

### Shadow Team
ANU undergraduate engineering students, tasked with reviewing this project to provide an external viewpoint on the outputs and governance of the project. Shadow Team still to be formed

| Name | Email |
| --- | --- |
| Elton Lu | u6096527@anu.edu.au |
| Patrick Dunphy | u6052409@anu.edu.au |
| Phillip Pulford | u5809328@anu.edu.au |
| Sha Shaharuddin | u5988860@anu.edu.au |
| Zachary Mason | u6080840@anu.edu.au |
| Ze Gan | u6051306@anu.edu.au |

#### Responsibilities of the project team to the shadow team
* Provide shadows access to all information surrounding the project, including repositories, documentation and relevant communications.  This information should be up-to-date and presented appropriately.
* Be open to feedback from all channels from shadows, and act on feedback appropriately.

#### Responsibilities of the shadow team to the project
* Remain up-to-date with the activities, outputs and governance of the project through information that is supplied to them.
* Commit to providing constructive, accurate and actionable feedback to the project through the pathways provided to them: including formal audit feedback, as well as verbal feedback in tutorial sessions and through the feedback forms supplied.

### Course Tutor
Jenny Simmons (jenny.simmons@anu.edu.au)

ANU ENGN4221 course tutor for Semester 1 2019. Tasked with formally organising and directing weekly tutorial sessions where the project is planned, presented and reflected upon.

#### Responsibilities of the project team to the course tutor
* Provide the tutor access to all information surrounding the project, including repositories, documentation and relevant communications. This information should be up-to-date and presented appropriately.
* Be open to feedback from the tutor, and act on feedback from all channels appropriately.
* Be present and prepared at all weekly tutorials (Tuesday 10-12), appropriate to the activity of the tutorial that week.
* Be informed of the structure of the course and related assessment milestones as established by the course convenor.
* Be prepared to submit assessments, and be open to grades and discussion of grades with the course tutor.

#### Responsibilities of the course tutor to the project
* Be present and prepared to lead the tutorial each week, appropriate to the activity of the tutorial, and remain up-to-date with the progress of the project.
* To a reasonable extent, assist the project team with the progress of the project, including answering relevant and reasonable questions, and providing constructive, actionable and accurate feedback, particularly at times of project audits and during tutorial sessions.
* Reply to correspondence (email) in a timely fashion, and grade formal assignments fairly and appropriate to the quality of the project.

### Course Convenors
Ankur Sharma (ankur.sharma@anu.edu.au)

ANU ENGN4221 course convenor for Semester 1 2019. The course convenor is the overall authority and organiser for this course, and hence this project as a subdivison of the course.

Chris Browne (chris.browne@anu.edu.au)

Former ANU ENGN4221 course convenor for Semester 1 2019. Advisor to the primary course convener.

#### Responsibilities of the project team to the course convenor
* Same as those applying to the course tutor.

#### Responsibilities of the course convenor to the project
* Same as the course tutor with the addition of:
* Organise the course appropriate to the desired outcomes and be receptive to feedback regarding this structure. Information regarding the structure and assessment milestones of the course should be available to students within a reasonable timeframe.

### Users
Members of the public, particularly students and educators who wish to utilise the device for educational purposes.

#### Responsibilities of the project team to the users
* Provide members of the public access to information that pertains to all aspects of the project.
* Design a device that is safe, stable and provides value.

#### Responsibilities of the users to the project
* Members of the public have little steadfast responsibility to the project team.
* Ideally, members of the public will provide feedback on the function of the device during requirements analysis or testing.

---

## Resources
The [Bill of Materials](/Hardware/Estimated%20Financials.xlsx) (BoM) outlines the current components of the device and their respective costs. The BOM will be regualrly updated as the choice of hardware is more refined as the project contiunues. The BoM will also be used to show what the procurement and research the team has arranged for component pricing with potential suppliers.

### Tools
With the potential to continue development with componentry, the tools likely to be used throughout this project include:
- Soldering Iron
- 3D Printer
- Laser Cutter
- Dremel
- Screwdriver, screws, nuts and bolts.

All safety precautions outlined by the ANU Makerspace's Terms and Conditions will be followed during the use of instrument or tool, regardless of where and how it is used. A safety risk analysis has been performed at the bottom of this document.

#### Project Administration
* GitHub
* Google Drive
* Discord (Primary Communications Platform)

#### Manufacturing and Testing
* Ian Ross Design Studio
* ANU Makerspace

#### Programming
Source code from the last semester of development will be modified for the optimisation of the current platform, or rewritten if deemed appropriate. A snapshot of the code has been captured and archived within the [repository](/master/Software/Initial%20Code). The code will be written on the Linux platform using Python and C++ programming languages, with all relevant extenral code referenced in the repository. 

## Project Management
### Deliverables
The initial deliverables are as follows:

#### Deliverables
* Determine the suitability of the current hardware and confirm final hardware solution.
* Optimise the software for the desired hardware to run more efficiently and detect veins more clearly to meet the desired system [requirements](Administration/Project/Requirements.md).
* Compile a list of procurement options and outline sources for the client to then purchase and build the kit for distribution.

### Milestones
Further detail on the optimisation of milestones and objectives of the project are detailed in the Requirements document.

#### Milestone 1
Decide on final hardware appropriate for the project's commercial vision.

#### Milestone 2
Optimise software to run as efficiently as possible for the desired hardware platform(s). Enclosure designs finalised.

#### Milestone 3
Compile quotations for external manufacture of components (PCBs, case, etc.)

#### Milestone 4
A kit of compiled components ready for the client for commercial distribution.

### Audit Goals
#### Audit 1
* Complete ConOps Version 1
* Reach Milestone 1

#### Audit 2
* Update ConOps to Version 2
* Complete requirements analysis
* Reach Milestone 2

#### Audit 3
* Achieve Milestone 3/4 with accompanying verification and validation

Milestones are subject to change as the project evolves. Changes will be made to this document to reflect project's new objectives.  

### Work Breakdown Structure
| Task | Time Allocation | Responsible Team(s)/Third Party | Status |
| --- | --- | --- | --- |
| ***1. Requirements Analysis***  |  | | |
|  -- 1.1. Review PoC   | 3 hours | All Teams | Complete |
|  -- 1.2. Perform risk analysis  | 1 hours | All Teams | Complete |
|  -- 1.3. Brainstorm requirements (in-house)   | 1 hour | Each Team Individually, Primary Client | Complete |
|  -- 1.4. Develop requirements with client | 1 hour | All Teams, Primary Client | Complete |
|  -- 1.5. Finalise requirements  | 2 hours | Each Team Individually| On going | 
| ***2. Prototyping***  | | | |
|  -- 2.1. Design new prototype  | 6 - 10 hours | Hardware | Complete |
|  -- 2.2. Manufacture and construct newest prototype | 4 - 8 hours | Hardware | Complete |
|  -- 2.3. Design base software in line with new requirements  | 6 - 10 hours | Software | Complete |
|  -- 2.4. Integrate software  | 2 hours | Software | In Progress |
|  -- 2.5. Update software with stretch deliverables  | 4 - 8 hours | Hardware | Awaiting Completion (Dependent on 2.3, 2.4) |
| ***3. Validation & Verification***   | | | |
|  -- 3.1. Test prototype in-house  | 4 hours | All Teams | In Progress |
|  -- 3.2. Conduct performance review  | 2 hours | All Teams (Primarily Governance) | Awaiting Completion (Dependent on 3.1) |
|  -- 3.3. Finalize Software  | 2 - 6 hours | Software | Awaiting Completion (Dependent on 3.1) |
|  -- 3.4. FInalize Bill of Materials | 2 hours | Hardware | Awaiting Completion (Dependent on 3.1) |
| ***4. Documentation***  | | | |
|  -- 4.1. Write ConOps v1  | 4 hours | Governace | Complete |
|  -- 4.2. Update ConOps to version 2  | 2 hours | Governance | Complete |
|  -- 4.3. Create poster  | 2 - 5 hours | Governance | Awaiting Completion (Dependent on 3) |
|  -- 4.4. Keep Repository Organised  | 3 - 8 hours | Governance | On going |

### Decision Making and Conflict Resolution
Decision making will be by consensus in consultation with the client. When consensus cannot be reached the project team will seek advice from other stakeholders depending on the nature of the decision. For further detail please refer to the [Decision Log](https://github.com/chrisbodger/veincam2019/blob/master/Administration/Project/Decision-Log.md).

---

## Risk Analysis
All risk analysis performed throughout this project will be in accordance to the Australian and New Zealand Industry Standard AS/NZS 4360:2004.

Risk Matrix

Potential risks to the success of the project have been brainstormed in order to understand them and mitigate either their severity or likelihood.

| Risk | Consequences | Likelihood | Severity | Mitigation |
| :---: | :---: | :---: | :---: | :---: |
| Not clearly understanding or defining requirements for the project. | Product does not meet requirements, primary client dissatisfied, requires re-doing work, going over budget and schedule to redesign | D | 3 | Maintain regular contact with client regarding progress and milestone completion. |
| Not defining scope of project and setting clear and achievable milestones. | No clear definition of project progress, feature creep over time results in lack of physical product, no clear "stopping point" for project or completed product, client dissatisifed, product does not meet customer requirements, likely to be over-budget. | C | 3 | Defining scope early and ensuring we stick to milestones and their respective outputs to ensure we do not deviate on a project tangent. Meeting (at minimum) weekly to discuss progress and next actionable deliverable for each team member, who is then held accountable for achieving that deliverable in the given time frame. |

### Safety Risk Analysis
In developing the prototype there is a chance of injury, similar to above these risks have been listed and steps taken to mitigate their severity or likelihood.

| Risk | Consequences | Likelihood | Severity | Mitigation |
| :---: | :---: | :---: | :---: | :---: |
| Personal harm whilst using listed tools (incl. burns, shocks, cuts) | Pain, discomfort and possible medical attention. | D | 3 | Ensuring all team members are familiar with the safety training of the ANU Makerspace/Engineering workshop, supervision by one other team member when using potentially dangerous tools. |
| Damage to Hardware due to physical impact or electrostatic discharge (ESD) | Loss of data, hardware faliure, schedule delays to order and replace damaged hardware. | E | 4 | Ensuring hardware is never placed in an area where it is likely to be damaged, always in full visible sight. Observing proper ESD safety techniques, such as regularly grounding ourselves and only contacting circuitry by edges. |

---

## References
[Venenfinder Github](https://github.com/Myrijam/Venenfinder)

[Venenfinder Hackaday.io Page](https://hackaday.io/project/26158-assistance-system-for-vein-detection)

[Veincam Stage 1](https://github.com/chrisbodger/veincam)

---

This Project is licensed under the Creative Commons license.

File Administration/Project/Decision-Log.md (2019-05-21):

 # Decision Log
 Created: 12/03/19

| Category        | Decision           | Date  |  Week | Risk To Project | 
| :-------------: |:-------------:| :-----:| :-----:|  :-----:|
| Whole system      |Look into **two versions of system with different levels of sophistication and functionality**. This will aim to cater to users that are merely interested in the system for entertainment purposes and those who wish to apply the device for advanced educational use. This will involve selection use of the Raspberry Zero and Raspberry A+ platform.  | 12/03/19 | 3 | H |
|Software|Decision to code in Python instead of C++. This is due to knowing that everything works in Python and not wanting to rewrite everything in C++.|12/03/2019|3| L |
|Hardware| Option of adding a **built-in battery has been dissolved**. Adding a built-in battery will increase build cost, board complexity, as such impacting on automated assembly, risk of failure and product return. Ben has noted that there is not substantial enough saleable benefit to be gained as to justify said cost and risk of a built-in battery.|19/03/19|4| L |
|Hardware|Boards for the Zero and Plus versions will be produced in red and blue, respectively. The viencam.org url and version number to be added to the boards.|23/03/19|4| L |
|Governance|Following Audit 1 feedback, discussed with primary client the relevance of requiring ANU Ethics approval. Given the goal of this project is to design a commercial kit, not commercialise a product, go to market, or test it publically, the decision has been made to not seek ANU Ethics approval. |24/03/2019|5| M |
|Whole system|Until software is verified the need and/or potential for two verions of the system is uncertain. Therefore it is decided for software to be verified prior to final decision whether or not to deliver several versions.|26/03/19|5| H |
|Whole system|During meeting with client, discussed first performance impressions of new image streaming on Raspberry Pi A+ vs Raspberri Pi Zero W. Decided that we are likely to focus our development efforts (both software and hardware) on the larger A+ platform, with the potential to scrap use and design of the Zero W. If we do so, VeinCam Plus will simply be called VeinCam.|7/04/19|6| M |
| Whole system | Due to both lack of performance and mechanical design issues with the Raspberry Pi Zero, it has been scrapped and design will go forward on only the Raspberry Pi 3A+ platform. |  15/04/19 | 7| M |
|Software| Based on VeinCam's performance in the lighting conditions at Bonython Primary School, made the decision to include a YUV image capture and processing stream as an optional setting. This was the old method used by the previous VeinCam team. Drastically reduces framerate but because image processing is performed on a local image file, image quaity is improved. |2/05/2019| 8 | M |
|Software| Made decision to focus more on educational aspect of VeinCam and include facts about the cardiovascular system, veins in a human arm, etc. in the user interface, so that students can actively engage with the software and learn more about the body. This feature will be implimented prior to the Poster Presentation. |13/03/2019| 10 | M |

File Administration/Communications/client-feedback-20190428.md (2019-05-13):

Hey guys.

Thanks for the img file.  I managed to get it and have created a shrunk version (~3.3GB). Just be aware that if you use this it will go through an expansion process the first time you boot (can go on different sized microSDs), which takes a while. It'll reboot itself when done.

I got the A+ up and running relatively easily with the hardware and software provided - thanks for that.

Based on where things are now, here are my thoughts.

## Hardware:
* Nicely done! Everything fits together well, maintains the key promises of the kit, and seems robust (didn’t break when I’ve dropped it!).
* On first run (prior to adjusting the camera focal length) I was getting a number of circular artifacts from in the image, which I think was due to the light interacting with the edges of the LED circular cutouts in the case. This might be resolved by making the cutouts much larger. Indeed, that would also be useful if opaque versions of the case are produced.
* Adjustment of the camera lens appears to be essential to producing a usable image. Is there any way to make this a simple process for users and reducing the risk of camera damage for them?  I used a pair of tweezers to make the adjustment, but this is probably not ideal.  I know mention was made of incorporating a tool into the case design - any further thoughts on that?
* It appears the MidOpt IR filter (3mm thick) is better.  Is that your impression too?  If so, then is there a way to make it smaller by a couple of mm (eg from 9mm to 7mm diameter), and to use a flexible spacer to enable this while excluding visible light?  Perhaps there is an off-the-shelf thin black rubber spacer that would do the trick. This way the 3mm filter might fit entirely within the clear case (rather than sitting proud) which will protect it better, and the spacer will allow for both a smaller diameter and accommodate variation in the depth of corner hole spacers once screws are tightened.  
* Related - I’m keen to hear what you think of the different filter options.  Is the acrylic as good as glass?  Is the midopt (3mm) acrylic better than the Edmund (1mm) acrylic?
Is there any particular path the cable should take when putting it together?  My guess is quite twisted, but works fine.  I’m wondering if I’ve got it wrong.
* As I think was mentioned, the notch for the microSD is a little short at the moment - still need a set of pliers to pull it out, and having the nuts flush with the end of the bolt would be nice.  I think you are already onto that.

## Software:
* I’ve not had a chance to take an in-depth look at the detail as yet, sorry, but you’ve made good progress.  Here are my thoughts so far:
### Image/quality.
* The frame rate is clearly a huge improvement for usability, and with camera adjustment the clarity is good.  With the after-processing there were quite a few linear artifacts at the frame rate, which it will be important to resolve as possible as they significantly distort the view of key veins (which also tend to be linear).  These were also an issue when I was developing for the Zero, and I think relate to the CLAHE settings relative to the size of the region-of-interest size.  However, since you may not have played with those settings, they may relate to the frame rate and shift to video rather than still processing.  In which case, I wonder if throttling the frame rate down a little (20-25?) will help resolve them.
* I think focusing on removing as many processing artifacts as possible will be important.
* Time to first page load.  I think of ‘setup’ speed as till the user can load the app page.  This has two components:
* Boot speed - time till a hotspot is accessible. Currently around 30-35s
* Is there someone working on cutting this time by going straight to a hotspot setup (rather than attempting to poll for a local network)?
* App load speed. Currently ~10sec from starting the app to getting the flask server running.  
* Do you know how much of this time is CV2 load?
### Light pin mapping.
* I think setting ‘1’ for light is off entirely at the moment, with ‘2’ being a minimal setting but with all lights on.  Is this due to the board design (ie, is it not possible to address the 2 set of LED circuits - 3v vs 5v - independently now), or is it just a software decision?
* Sorry the feedback is limited at this point - I’ll can give more later, and am happy if you have specific things you want me to look at.  

## Audit feedback:
* I’ve taken a look at this and agree that progress has been great.
* The main things I’d add or reinforce are:
* The need for focus with a roadmap of deliverables/priorities, laid out by the time left on the project (active device development time, rather than presso prep and event prep).  Can you guys put one together?  Focus will likely need to be more on software than hardware, since I get hardware is now up to fine tuning phase.
Related to this, I’m presuming the team is now only developing on/for the A+ (a decision I support).  Please let me know if that’s not the case.
* Considering a shift in roles toward more software team members.  There are three streams (in order of priority) in which software development is likely to make gains:
* Image quality (since this is the key selling point / promise of the device)
* Time to first page load
* Modifying / tidying user interface

And thanks again for your hard work and enthusiasm to date - I know my involvement has been limited by availability but you’ve been a very easy group to work with!

Cheers,
Ben.

# Actionables
### Hardware
* Increase LED cutout size for optical clarity
* Easier method to adjust camera lens (bundled tool made from a cheap material, thin acrylic perhaps?)
* Definitive testing of IR acrylic filters - shrink diameter of 3mm filter and make flush with top plate
* shorter camera cables?
* make SD card notch larger - cannot remove from device without tools

### Software
* clear up linear artefacts
* look into CLAHE
* boot time reduction - remove polling for local internet
* app profiling - anyway to reduce load times further? how much of it is CV2?
* Light Pin mapping - dimming settings (3V and 5V rail access by both LEDs) 

# Comments

## Hardware

* Cool!
* We hadn't noticed that before, will make the holes larger to ensure it dosen't happen. 
* Will add a cutout to the bottom plate which mates with the camera lens and allows adjustment. 
* The SW guys (who have the VeinCams) agree that 3mm is better. We have an idea which will get the IR acrylic down to 5mm dia whilst ensuring that is sits flush. Josh will get a new set of prototypes cut end of week and go from there. 
* We know the cable routing sucks, shoving it in there seems like the best option without replacing the FFC for a shorter cable. Could be done but would add >$5 per VeinCam which I (Josh) would prefer not avoid. 
* We were thinking that it would be good to hide the SD card to stop kids pulling it out, but added the indent so it can still be removed. Thoughts? Happy to make it anywhere from real easy to really hard to remove. 
* We were unable to source the correct length / dia screws locally, have ordered correct parts and most have arrived, only the M2.5 nuts are left and it will all be flush.

## Software 
* Linear Artifacts were tied to refresh rate of the lEDs with respect to the camera frame rate, we were able to fix this via changing the LED refresh rate so that camera frame rate period was an integer multiple of the LEDs refresh rate period (hope that makes sense), although you can still sometimes notice them, its a very significant decrease
* We agree, at the moment most of the artifacts now come from the IR acrylic itself and also the camera focus. After extended use I have also noticed the IR acrylic can smudge easily making the image more blurry, though of course having the correct camera focus provides the biggest benefit
* We have done many boot time measurements and the vast majority of this time is just the pi booting normally, the actual setting up of the hotspot takes around 3-5 seconds, and removing those lines of code does not seem to make any difference to that small time window
* Yes the server takes around 10 seconds to load the first time it is booted, but from what we have tested opencv is only around a third to half of this time. There still seems to be a fair bit of inconsistency out there when it comes to what you should and shouldn't be removing from opencv, but the benefit may not even be a seconds worth of boot time. Of course we do not know this for sure, but this is going on percentages from other results online.
    * Following on from this we are still investigating the possibility of providing an initial page render with a loading gif so the user can at least have that for the 8 seconds or so it takes for app.py to run its imports, creating the illusion of less down time but of course its not as high on the priority list as others though we do already have the gif made to pass on to you if we do not get around to it
*Light Pin Mapping
    * (Josh here) It's not a hardware issue, all LEDs of the same nm are controlled at the same time, probably a quick software fix.

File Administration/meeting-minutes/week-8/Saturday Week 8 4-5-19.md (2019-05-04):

# Meeting Minutes Saturday Week 8 4-5-19

## Participants
|Present|Absent|
|:---:|:---:|
|Josh||
|Chris||
|Alex B||
|Alex O||
|Tom||
|Patrick||

## Agenda
1. Ben's feedback
2. Project discussion

## Governance
* Ben has noted that we have potentially looked into the wrong market with kids at primary school. This was a misunderstanding however; this was opted for as it was provided by the ANU. The goal was to gain the connection in Sarah Fletcher from the Science industry. This connection with the school science director, who has great influence upon the science curriculum is very signficant to the progress of Veincam. Sarah has noted it not so much the technical side of things, but about the teaching of failure to kids and having a more open and adaptable educational tool.
* If Ben has no interest in providing the Veincam for educational purposes, it is uncertain that medical schools will opt for such technology as the Veincam doesnt do a good enough job for such applications. However, this is not our problem to consider, and is Ben's.

## Software
* Ben is happy with the current image quality; we are not to continue to improve this with the prospect for marginal improvement with a lot of effort.
* To implement a switch option between old and new method of image capture to then compare image processing and quality.
* Potential to implement a pause button; we'd be able to go from 20fps to a still image; actually pause the stream. This will enable the user to look at said captured image. Hence pause will display as still capture until resume is selected to prompt streaming.
* Attempt to remove linear artefacts.
* Ben does not necessarily care about the front end and associated improvement in these area.

## Hardware
* Ben is generally happy with the progress and status of hardware currently.
* Concern of camera out of the box's focus is terrible. If we can integrate a tool into the casing, then the fitting will be better. If its not screwed out a little bit you will still need plyers. If we need to use other tools to grab the camera, this may be annoying by worhtwhile to not damage the camera.
* SD cut out vs no SD car cutout; will aim to leave as is as it is able to be taken out if necessary but not so easy that kids/users can easily pull out the SD when the Veincam is running.
* Acryilic is to be shrunk to the diameter of the outer cell, and there will be a spacing between the camera and acryllic.

## Actionables
* Aims to finalise all aspects of the project for handover.

### Hardware
* To finalise laser cutt-outs for pricing.

### Software
* Make sure switching between old and new methods work.
* Clean up main script and do some commenting where required.
* Write a document on how functions work for future teams.
* Rest of efforts to be given towards removal of linear artefacts.

### Governance
* Gain contact with Gunghalin College.
* Finalise poster.
* Clean up repository.
* Get everything ready for handover.

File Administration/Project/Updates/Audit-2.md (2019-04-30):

#### Hardware
Hardware has been busy designing and testing new case designs, with the case for the VeinCam Plus being close to being finalised. 
Currently awaiting more parts to arrive before case design for the VeinCam Zero begins. 
Printed Circuit Boards have arrived and been assembled, prelimary check shows them working as planned, will have to wait for software to add some code before full functionality of the printed circuit boards.

### Software

With this major hurdle out of the way we plan to begin improving the image processing algorithm, improving the user front end and cleaning up the Python files.

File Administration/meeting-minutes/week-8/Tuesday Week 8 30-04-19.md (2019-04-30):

# Meeting Minutes Tuesday Week 8 30-04-19

## Participants
|Present|Absent|
|:---:|:---:|
|Josh||
|Chris||
|Alex B||
|Alex O||
|Tom||
|Patrick||

## Agenda
1. Ben's feedback
2. Audit feedback
3. Project discussion
4. Tutorial meeting

## Main Discussion
### Governance
* Aim to be better in harmony with what Ben expects and what subteam priorities are.
* Need to clarify what educational experience/resources we aim to present students with and how we aim to do so. While the education/involvement of students is important we are prioritising teacher feedback. Must develop questions that we want to be asked as feedback.
* To consider poster and development on this from last semester.

### Software
* Histogram equalisation failing to be optimised. Linear artefacts are presents. This may simply be the tradeoff for high frame rates; therefore simply can't resolve the presence of linear artefacts. Ben thinks its an issue of the Histrogram settings - Patrick has played with said settings sufficiently. This issue has surely been overcome by someone else and is therefore worth investigating, but not absolutely critical.
* Ben believed that boot up time is ~32 seconds and that this was attributed to hotspotting; the Raspberry Pi can be attributed to this first ~30 seconds. Therefore it is all prior to any code running. This improvement is not critical. Image processing is more important.
* Change brightness settings for LEDs. Include on/off button and 1-5 brightness or the like. Decided on 3 modes; off, medium and high; 0,1,2,3. (Decision log)
* Image quality and boot time can't be improved much more with the power we have. User-interface can be improved to enhance the user experience and educational understanding.

### Hardware
* Circular artefacts. Ben noticed said artefacts when testing Veincam.
* Add tooling shaped on the back of the case so you can adjust the lense when everything is assembled.
* Tightening of lense greatly impacts on image quality; focus is highly sensitive to tightening. The kit works fine however without agjusting for optimal iamge quality. For the general case this is therefore probably not an issue; most kids won't care or notice the difference.
* Filter: Size of acrylic to be reduced; expensive component that Ben want to reduce cost of, however optimising clarity and image quality mandates it.
* Ribbon cable is twisted due to being unnecessarily long. This is a minor issue as we can't buy shorter ones.
* Notch for microSD. Group believes that having the microSD inaccessible is probably better. It will most likely be the case that only teachers will be assembling the kit. Having the SD inaccessible to students who  may destroy the hardware is important. (Decision log)

## Decisions Made
* Notch for microSD. Group believes that having the microSD inaccessible is probably better.
* Change brightness settings for LEDs. Include on/off button and 1-5 brightness or the like. Decided on 3 modes; off, medium and high; 0,1,2,3.

## Deliverables
* Governance to attend Monday session regarding poster presentation and begin work on this.
* Governance to develop feedback questions for teacher for school presentation.
* Hardware and Software to consider Ben's feedback; filter, LED brightness settings.

## Tutorial Meeting
* Governance to attend poster session on Monday.
* Whole team to ensure that there is appropriate evidence and documentation that will be used to support or substantiate claim of grade later in the semester.

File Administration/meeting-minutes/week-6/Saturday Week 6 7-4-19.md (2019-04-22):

# Meeting Minutes Saturday 7/4/19

## Agenda
1. Meeting with Client
2. Project discussion

### Hardware
* Ben has noted the thought process behind delivering two devices. Evidently that we are aiming to prove use case of having two soon. The idea is to decide as a group, but specifically to determine which version provides the best performance and just go with that option. Still working on both hardware platforms until software is finalised. When this occurrs we can decide to commit to the build of the one.
* Looking to focus merely on VeinCam Plus and scrap the Zero. Aim to have this decision finalised. It would be nice to keep both models and do testing with both and also have the two models for future teams, however. Financial consideration is that prices for boards will be increased if we were to buy both versions, and will be reduced if we go all in on one.
* Thinking of continuing with acryclic cases.
* The Pi camera; manually focusing the lense improved the performance and clarity. How will we consider this? Once assembled, you have to pull the case apart to adjust the camera. This consideration is worth looking into when we start getting prices.
* Ben is interested in headers and making them solderless. We are aiming to get the manufacturer to do the soldering for the boards. Also noted was that from china headers are 10c each.
* We've currently laser cut out a hole for the camera; consideration for taking care to not impact the camera lens.
* Ben has noted that we should consider that shape of which we are currently cutting acrylic; could go a square with rounded corners or the like to reduce the material wasted.
* Ben also noted the remapping of pins given new circuit board layout; the Pi has pulse width modulation (PWM) and theres only a few a number of pins that map to PWM. Ben wanted to check that this had been considered, which it has. 
* Licenses are all compatible with GPLV3; this is to be noted in repository.
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

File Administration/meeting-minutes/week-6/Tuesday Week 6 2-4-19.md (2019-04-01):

# Meeting Minutes Tuesday 2/4/19

## Participants
|Present|Absent|
|:---:|:---:|
|Josh||
|Chris||
|Alex B||
|Alex O||
|Tom||
|Patrick||

## Agenda
1. Project Discussion
2. System testing

## 1. Project Discussion
### Hardware
* Testing and designing of new case designs has occurred. The VeinCam Plus case is close to finalisation. We are currently awaiting the arrrival of parts. Once this happens, the design for the VeinCam Zero will begin. Printed Circuit Boards (PCBs) have arrived and been assembled, with initial checks working properly. Full functionality may be tested when software has developed the code further.
* Once assembled, the removal of the SD card becomes very difficult (we need tweezers or the like). This is a further consideration for design for protecting the SD card.
* LEDs are working.
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

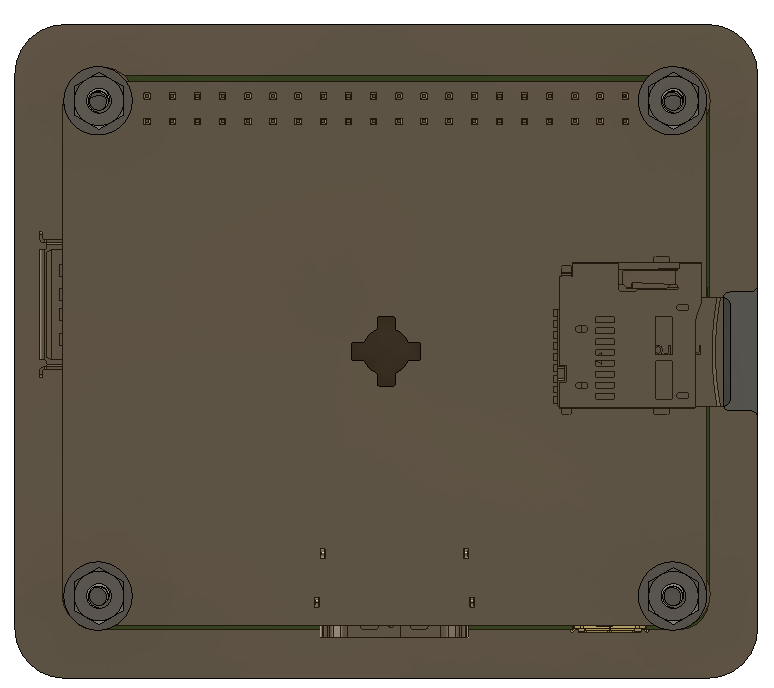
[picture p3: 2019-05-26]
Hardware/ProductionOutputs/Renders/bottom.PNG

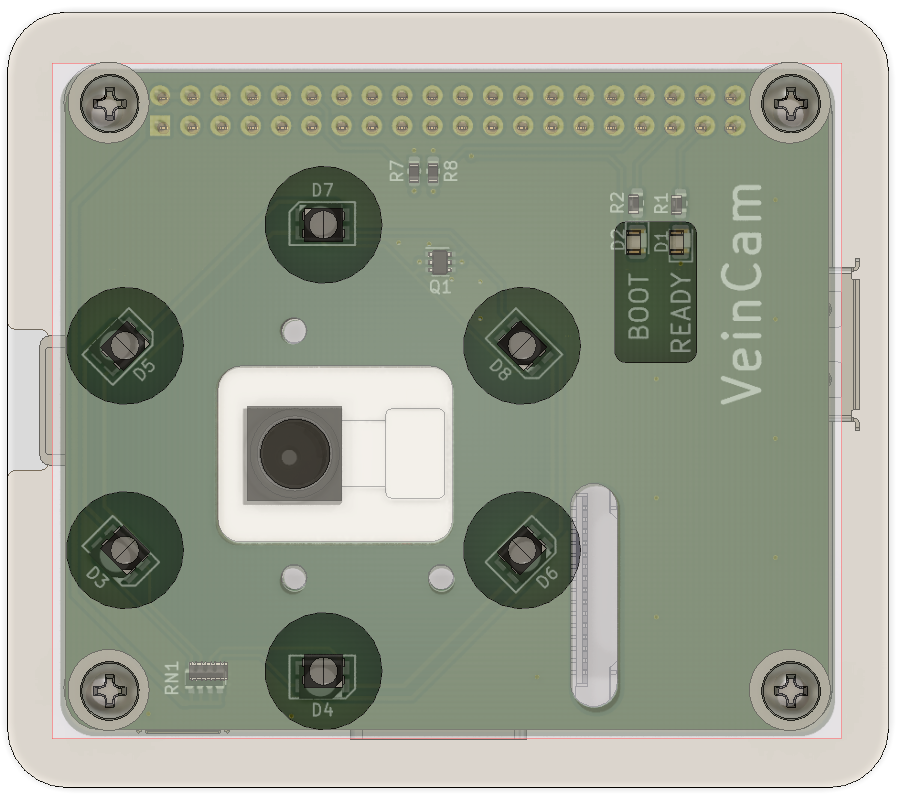
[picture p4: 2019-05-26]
Hardware/ProductionOutputs/Renders/topWithOverlay.PNG

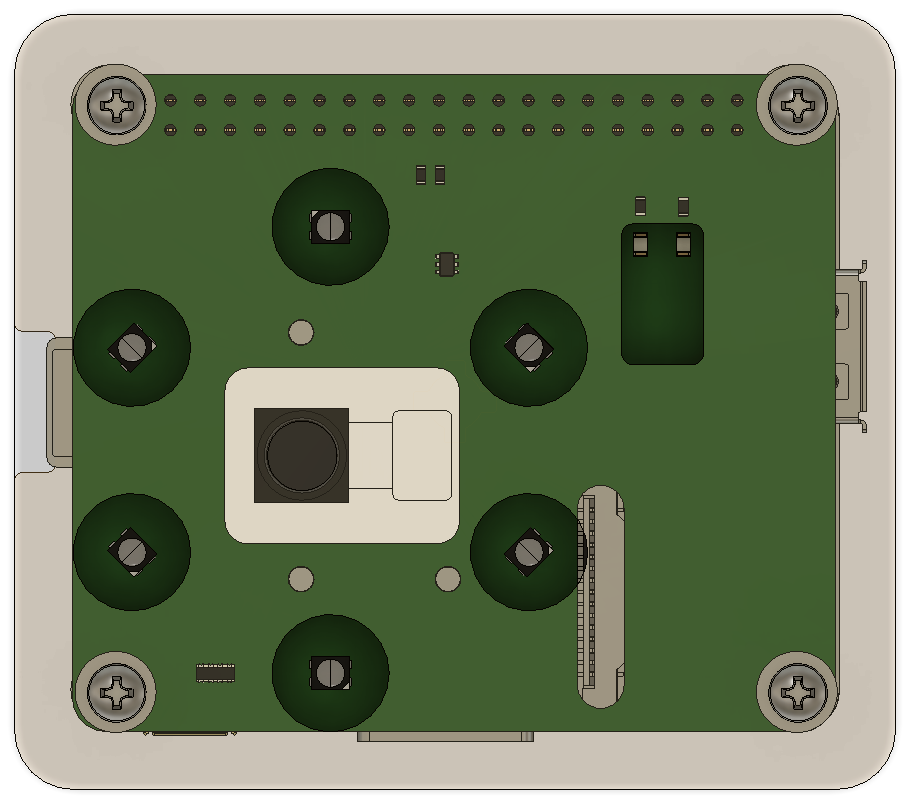
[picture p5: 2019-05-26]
Hardware/ProductionOutputs/Renders/top.PNG

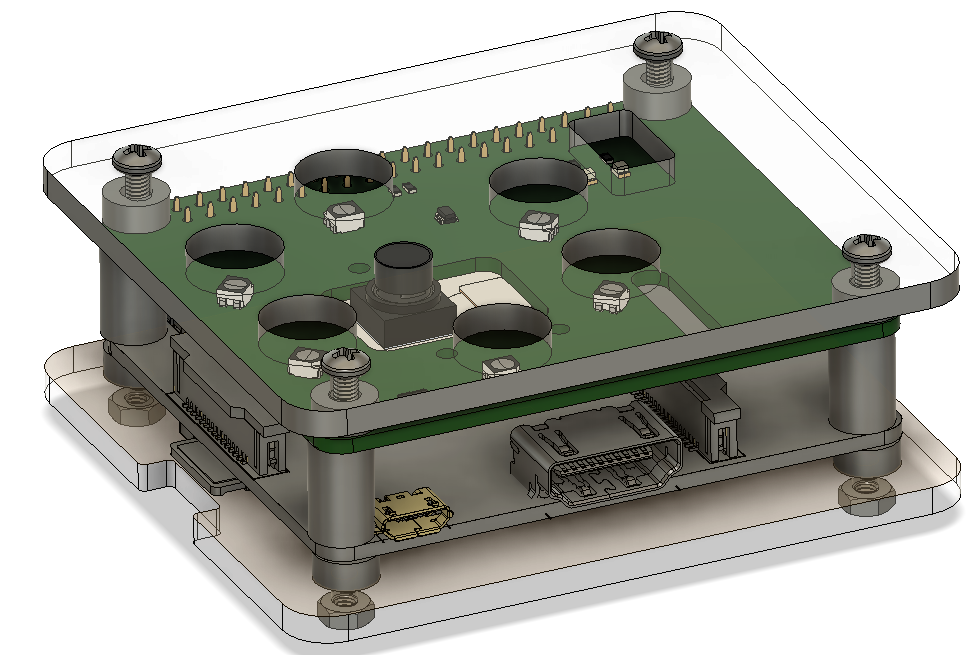
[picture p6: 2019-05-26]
Hardware/ProductionOutputs/Renders/side.PNG

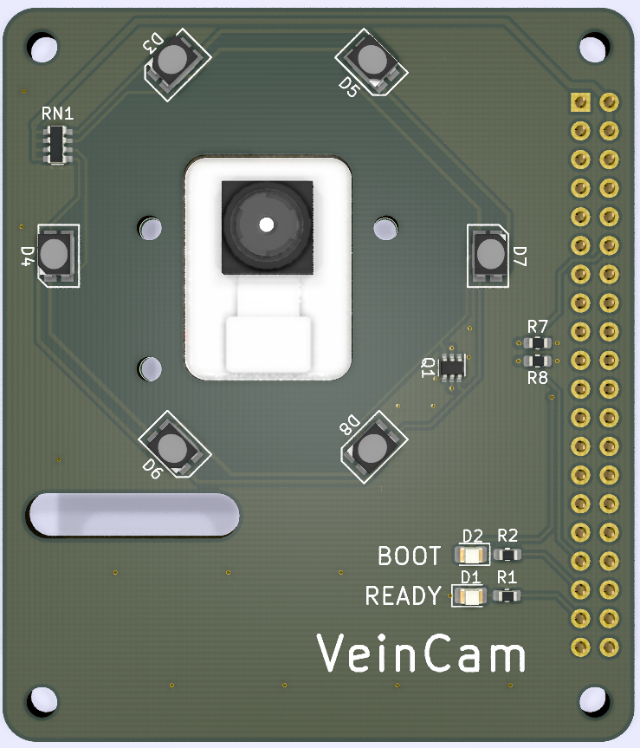
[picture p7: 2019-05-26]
Hardware/ProductionOutputs/Renders/PCB.PNG

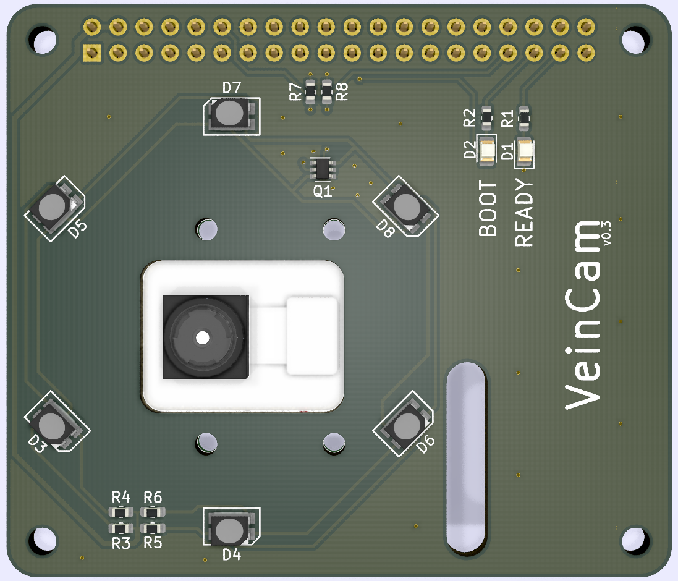
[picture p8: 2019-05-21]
Hardware/VeinCamHat/Render.png

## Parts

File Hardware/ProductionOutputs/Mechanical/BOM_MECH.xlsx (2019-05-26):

Mounting Hardware | Quantity | Cost ea | Cost total | Supplier
M2.5 * 28mm Screw | 4 | $0.11 | $0.43 | https://www.ebay.com.au/itm/M2-5-3-60mm-Pan-Head-Phillips-Screws-Machine-Screws-Bolts-G304-Stainless-Steel/273041450256?ssPageName=STRK%3AMEBIDX%3AIT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
M3 * 11mm Spacer | 4 | $0.06 | $0.23 | https://www.aliexpress.com/item/50pcs-M3-M4-M5-M6-M8-White-Nylon-ABS-Non-Threaded-Spacer-Round-Hollow-Standoff-Washer/32868508973.html
M3 * 3mm Spacer | 8 | $0.06 | $0.46 | https://www.aliexpress.com/item/50pcs-M3-M4-M5-M6-M8-White-Nylon-ABS-Non-Threaded-Spacer-Round-Hollow-Standoff-Washer/32868508973.html
M2 * 4mm Screw | 4 | $0.03 | $0.10 | https://www.aliexpress.com/item/100Pcs-50pcs-m1-m1-2-m1-4-m1-6-M2-M2-5-M3-M4-DIN7985-GB818/32948746653.html
M2.5 Nut | 4 | $0.03 | $0.13 | https://www.aliexpress.com/item/50Pcs-DIN934-M2-M2-5-M3-M4-M5-M6-M8-304-Stainless-Steel-Metric-Thread-Hex/32958861614.html
M2 Nut | 4 | $0.03 | $0.13 | https://www.aliexpress.com/item/50Pcs-DIN934-M2-M2-5-M3-M4-M5-M6-M8-304-Stainless-Steel-Metric-Thread-Hex/32958861614.html
 |  | Total Cost: | $1.49

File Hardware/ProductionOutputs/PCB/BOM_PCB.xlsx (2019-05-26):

Item | Qty | Reference(s) | Value | LibPart | Footprint | Supplier Link
1 | 1 | D1 | GREEN LED | Device:LED | LED_SMD:LED_0805_2012Metric | https://lcsc.com/product-detail/Light-Emitting-Diodes-LED_LED-green0805_C63855.html
2 | 1 | D2 | RED LED | Device:LED | LED_SMD:LED_0805_2012Metric | https://lcsc.com/product-detail/Light-Emitting-Diodes-LED_red-SMDLED_C86865.html
3 | 6 | D3, D4, D5, D6, D7, D8 | SFH7252 | VeinCam_Symbols:SFH7252 | VeinCam_Footprints:SFH7252 | https://au.mouser.com/ProductDetail/OSRAM-Opto-Semiconductors/SFH-7252
5 | 1 | J1 | Raspberry_Pi_2_3 | Connector:Raspberry_Pi_2_3 | Connector_PinSocket_2.54mm:PinSocket_2x20_P2.54mm_Vertical | https://lcsc.com/product-detail/Others_2685Y-220CNG1SNA01_C350295.html
6 | 1 | Q1 | NTJD4001N | VeinCam_Symbols:NTJD4001N | Package_TO_SOT_SMD:SOT-363_SC-70-6 | https://lcsc.com/product-detail/MOSFET_ON-Semicon_NTJD4001NT1G_ON-Semicon-ON-NTJD4001NT1G_C190019.html
7 | 1 | R1 | 1K | Device:R | Resistor_SMD:R_0603_1608Metric | https://lcsc.com/product-detail/Others_ResistorToday-ETCR0603F1K00K9_C365394.html
8 | 1 | R2 | 1K5 | Device:R | Resistor_SMD:R_0603_1608Metric | https://lcsc.com/product-detail/Chip-Resistor-Surface-Mount_ResistorToday-AECR0603F1K50K9_C328342.html
9 | 2 | R7, R8 | 10K | Device:R | Resistor_SMD:R_0603_1608Metric | https://lcsc.com/product-detail/Chip-Resistor-Surface-Mount_ResistorToday-AECR0603F10K0K9_C328335.html
10 | 1 | RN1 | R_Pack04 | Device:R_Pack04 | Resistor_SMD:R_Array_Convex_4x0603 | https://au.mouser.com/ProductDetail/Bourns/CAY16-3R0J4LF?qs=XW6UEr546KLbZW%2FumziEKQ%3D%3D
 |  |  |  |  |  | Depending on specific LEDs, R1 and R2 may need to be changed to set brightness of status LEDs
 |  |  |  |  |  | Suggest purchasing below to allow for swapping out of parts if required
 |  |  |  |  |  | https://lcsc.com/product-detail/Chip-Resistor-Surface-Mount_ResistorToday-AECR0603F2K00K9_C328350.html

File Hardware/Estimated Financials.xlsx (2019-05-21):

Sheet: VeinCam BOM
RPi 3A+, VeinCam, Clear Acrylic Case
Part / Assembly |  | Per Unit Cost (Quantity 1000) | Supplier
PCA |  | $6.78 | See VeinCamHat Sheet | Mounting Hardware | Quantity | Cost ea | Cost total | Supplier
Enclosure |  |  |  | M2.5 * 28mm Screw | 4 | $0.11 | $0.43 | https://www.ebay.com.au/itm/M2-5-3-60mm-Pan-Head-Phillips-Screws-Machine-Screws-Bolts-G304-Stainless-Steel/273041450256?ssPageName=STRK%3AMEBIDX%3AIT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
 | Clear Acrylic + Labour | $2.50 |  | M3 * 11mm Spacer | 4 | $0.06 | $0.23 | https://www.aliexpress.com/item/50pcs-M3-M4-M5-M6-M8-White-Nylon-ABS-Non-Threaded-Spacer-Round-Hollow-Standoff-Washer/32868508973.html
 | IR Filter Acrylic | $1.50 | Assuming $150 for 50*50mm | M3 * 3mm Spacer | 8 | $0.06 | $0.46 | https://www.aliexpress.com/item/50pcs-M3-M4-M5-M6-M8-White-Nylon-ABS-Non-Threaded-Spacer-Round-Hollow-Standoff-Washer/32868508973.html
 | Mounting hardware | $1.49 | Look in this direction -> | M2 * 4mm Screw | 4 | $0.03 | $0.10 | https://www.aliexpress.com/item/100Pcs-50pcs-m1-m1-2-m1-4-m1-6-M2-M2-5-M3-M4-DIN7985-GB818/32948746653.html
 |  |  |  | M2.5 Nut | 4 | $0.03 | $0.13 | https://www.aliexpress.com/item/50Pcs-DIN934-M2-M2-5-M3-M4-M5-M6-M8-304-Stainless-Steel-Metric-Thread-Hex/32958861614.html
Estimated Total |  |  |  | M2 Nut | 4 | $0.03 | $0.13 | https://www.aliexpress.com/item/50Pcs-DIN934-M2-M2-5-M3-M4-M5-M6-M8-304-Stainless-Steel-Metric-Thread-Hex/32958861614.html
 | Cost Price (ex GST) | $12.27
 | Cost Price (inc GST) | $13.49 |  |  |  | Total Cost: | $1.49
 | Sale Price | $39.99
 | Profit | $26.50
 | Markup | 196.3363666%
 | Delivery Cost | $8.30
Customer Supplied Items:
 | Raspberry Pi 3 A + | $38.23 | https://core-electronics.com.au/raspberry-pi-3-model-a-plus.html
 | PinoIR Camera Module | $38.95 | https://core-electronics.com.au/raspberry-pi-noir-camera-board-v2-8-megapixels-38553.html
 | 16GB mSD Card | $9.00 | https://www.officeworks.com.au/shop/officeworks/p/sandisk-ultra-16gb-micro-sdhc-memory-card-sdsq16gb
 | USB Cable / PSU | $12.95 | https://www.ebay.com.au/itm/50000mAh-External-Power-Bank-Dual-USB-Portable-Battery-Charger-For-Mobile-Phone/391554571425
 | Cost of Customer Items | $99.13
Total price to consumer
 | Excludes freight on self supplied items
 | Total | $147.42

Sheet: VeinCamHat BOM
Qty | Reference(s) | Value | Quantity Per 1000 | Per Unit Cost at Quantity (ex) | Cost Per Board | Notes | Supplier URL
6 | D3, D4, D5, D6, D7, D8 | SFH7252 | 6000 | $0.86 | $5.16 | 5 month lead time | https://au.rs-online.com/web/p/ir-leds/1685175/
1 | D1 | GREEN LED | 1000 | $0.02 | $0.02 | China Price shown | https://www.digikey.com.au/products/en/optoelectronics/led-indication-discrete/105?FV=ffe00069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
1 | D2 | RED LED | 1000 | $0.02 | $0.02 | China Price shown | https://www.digikey.com.au/product-detail/en/lite-on-inc/LTST-C171KRKT/160-1427-2-ND/386801
1 | J2 | 20x2 Pin Header Female | 1000 | $0.20 | $0.20 | China Price shown | https://www.digikey.com.au/product-detail/en/sullins-connector-solutions/PPTC202LFBN-RC/S6104-ND/807240
1 | Q1 | NTJD4001N | 1000 | $0.17 | $0.17 |  | https://www.digikey.com.au/product-detail/en/on-semiconductor/NTJD4001NT1G/NTJD4001NT1GOSCT-ND/687105
1 | R1 | 1k | 1000 | $0.01 | $0.01 |  | https://www.digikey.com.au/product-detail/en/te-connectivity-passive-product/CRGCQ0603J1K0/A130091CT-ND/8577923
1 | R2 | 1k5 | 1000 | $0.01 | $0.01 |  | https://www.digikey.com.au/product-detail/en/te-connectivity-passive-product/CRGCQ0603J1K5/A130091CT-ND/8577923
2 | R7, R8 | 10k | 2000 | $0.01 | $0.01 |  | https://www.digikey.com.au/product-detail/en/te-connectivity-passive-product/CRGCQ0603J10K/A130097CT-ND/8577929
4 | R3, R4, R5, R6 | 3R3 | 4000 | $0.01 | $0.02 |  | https://www.digikey.com.au/product-detail/en/te-connectivity-passive-product/CRGCQ0603J3R3/A130076CT-ND/8577908
 |  |  |  | Total Cost at Quantity
1 | PCB |  | 1000 | $500.00 | $0.50 | PCBWAY Estimate
1 | PCBA |  | 1000 | $460.00 | $0.46 | PCBWAY Estimate
1 | Freight |  | 1000 | $210.00 | $0.21 | PCBWAY Estimate
 |  |  |  | Total Per Board (ex): | $6.78

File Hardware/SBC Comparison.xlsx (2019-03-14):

Model | Raspberry Pi Zero W | Raspberry Pi 3 B + | Raspberry Pi 3 A + | OpenCamM7 | OpenCamH7 | BeagleBone Black Wireless | Orange Pi Lite 2
CPU | Broadcom 2835 ARM 1 GHz | Broadcom, Cortex-A53, 1.4 GHz 64 Bit | Broadcom, Cortex-A53, 1.4 GHz 64 Bit | STM32 Cortex M7 216 MHz | STM32 Cortex M7 400 MHz | Octavo OSD3358 Cortex-A8 - 1GHz | Allwinner H6 (Cortex-A53 64 Bit)
Number of Cores | 1 | 4 | 4 | 1 | 1 | 1 | 4
Ram | 512MB | 1GB | 512MB | 512k | 1MB | 512 MB | 1 GB
MIPI Interface? | Y | Y | Y | N/A | N/A | N | Y
Dimensions (mm) | 65*30*5 | 85 * 49 * 16 | 55*65*8.5 | 32*44*10 | 32*44*10 | 86*55*10 | 69*48*15
Price (Quantity 1) | $15.29 | $54.95 | $38.23 | $63.00 | $92.00 | $100.00 | $25.00
Comments

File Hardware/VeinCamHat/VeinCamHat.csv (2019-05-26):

Source: | C:\Users\Josh Johnson\Dropbox\ENGN4221\veincam2019\Hardware\VeinCamHat\VeinCamHat.sch
Date: | 26/05/2019 19:16:13
Tool: | Eeschema (5.1.2)-1
Generator: | C:\Program Files\KiCad\bin\scripting\plugins/bom_csv_grouped_by_value.py
Component Count: | 19
Individual Components:
Item | Qty | Reference(s) | Value | LibPart | Footprint | Datasheet
 |  | D1 | GREEN LED | Device:LED | LED_SMD:LED_0805_2012Metric | ~
 |  | D2 | RED LED | Device:LED | LED_SMD:LED_0805_2012Metric | ~
 |  | D3 | SFH7252 | VeinCam_Symbols:SFH7252 | VeinCam_Footprints:SFH7252 | ~
 |  | D4 | SFH7252 | VeinCam_Symbols:SFH7252 | VeinCam_Footprints:SFH7252 | ~
 |  | D5 | SFH7252 | VeinCam_Symbols:SFH7252 | VeinCam_Footprints:SFH7252 | ~
 |  | D6 | SFH7252 | VeinCam_Symbols:SFH7252 | VeinCam_Footprints:SFH7252 | ~
 |  | D7 | SFH7252 | VeinCam_Symbols:SFH7252 | VeinCam_Footprints:SFH7252 | ~
 |  | D8 | SFH7252 | VeinCam_Symbols:SFH7252 | VeinCam_Footprints:SFH7252 | ~
 |  | H1 | MountingHole | Mechanical:MountingHole | MountingHole:MountingHole_2.7mm_M2.5 | ~
 |  | H2 | MountingHole | Mechanical:MountingHole | MountingHole:MountingHole_2.7mm_M2.5 | ~
 |  | H3 | MountingHole | Mechanical:MountingHole | MountingHole:MountingHole_2.7mm_M2.5 | ~
 |  | H4 | MountingHole | Mechanical:MountingHole | MountingHole:MountingHole_2.7mm_M2.5 | ~
 |  | J1 | Raspberry_Pi_2_3 | Connector:Raspberry_Pi_2_3 | Connector_PinSocket_2.54mm:PinSocket_2x20_P2.54mm_Vertical | https://www.raspberrypi.org/documentation/hardware/raspberrypi/schematics/rpi_SCH_3bplus_1p0_reduced.pdf
 |  | Q1 | NTJD4001N | VeinCam_Symbols:NTJD4001N | Package_TO_SOT_SMD:SOT-363_SC-70-6
 |  | R1 | 1K | Device:R | Resistor_SMD:R_0603_1608Metric | ~
 |  | R2 | 1K5 | Device:R | Resistor_SMD:R_0603_1608Metric | ~
 |  | R7 | 10K | Device:R | Resistor_SMD:R_0603_1608Metric | ~
 |  | R8 | 10K | Device:R | Resistor_SMD:R_0603_1608Metric | ~
 |  | RN1 | R_Pack04 | Device:R_Pack04 | Resistor_SMD:R_Array_Concave_4x0603 | ~
Collated Components:
Item | Qty | Reference(s) | Value | LibPart | Footprint | Datasheet
1 | 1 | D1 | GREEN LED | Device:LED | LED_SMD:LED_0805_2012Metric | ~
2 | 1 | D2 | RED LED | Device:LED | LED_SMD:LED_0805_2012Metric | ~
3 | 6 | D3, D4, D5, D6, D7, D8 | SFH7252 | VeinCam_Symbols:SFH7252 | VeinCam_Footprints:SFH7252 | ~
4 | 4 | H1, H2, H3, H4 | MountingHole | Mechanical:MountingHole | MountingHole:MountingHole_2.7mm_M2.5 | ~
5 | 1 | J1 | Raspberry_Pi_2_3 | Connector:Raspberry_Pi_2_3 | Connector_PinSocket_2.54mm:PinSocket_2x20_P2.54mm_Vertical | https://www.raspberrypi.org/documentation/hardware/raspberrypi/schematics/rpi_SCH_3bplus_1p0_reduced.pdf
6 | 1 | Q1 | NTJD4001N | VeinCam_Symbols:NTJD4001N | Package_TO_SOT_SMD:SOT-363_SC-70-6
7 | 1 | R1 | 1K | Device:R | Resistor_SMD:R_0603_1608Metric | ~
8 | 1 | R2 | 1K5 | Device:R | Resistor_SMD:R_0603_1608Metric | ~
9 | 2 | R7, R8 | 10K | Device:R | Resistor_SMD:R_0603_1608Metric | ~
10 | 1 | RN1 | R_Pack04 | Device:R_Pack04 | Resistor_SMD:R_Array_Concave_4x0603 | ~

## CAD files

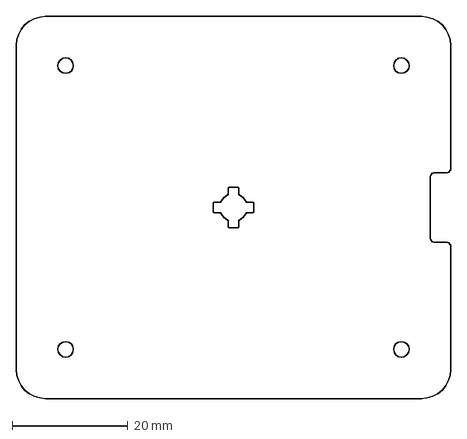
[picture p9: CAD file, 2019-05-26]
Hardware/ProductionOutputs/Mechanical/bottomCase.dxf
75.0 x 66.0 mm

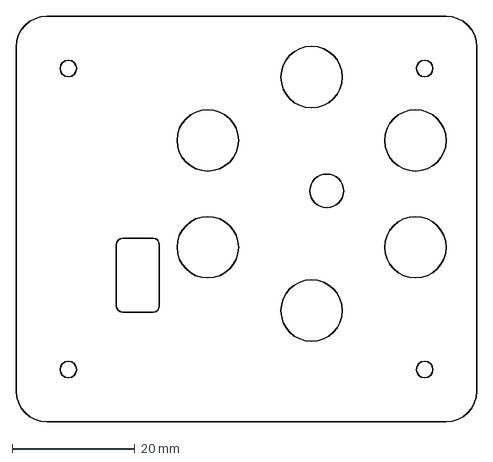
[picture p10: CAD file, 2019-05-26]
Hardware/ProductionOutputs/Mechanical/topCase.dxf
75.0 x 66.0 mm

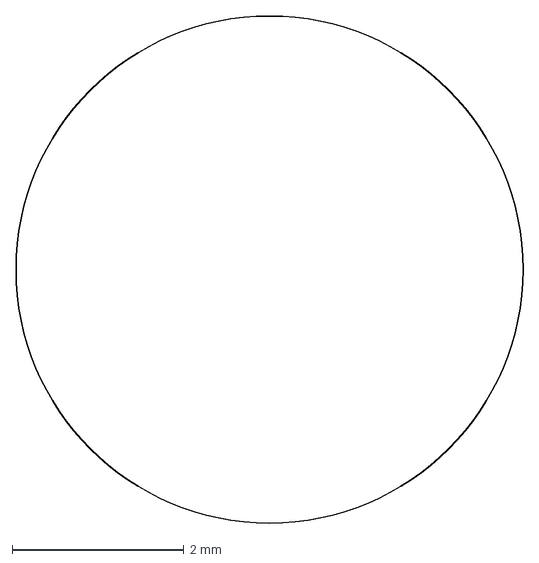
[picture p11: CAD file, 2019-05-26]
Hardware/ProductionOutputs/Mechanical/lens.dxf
5.90 x 5.90 mm

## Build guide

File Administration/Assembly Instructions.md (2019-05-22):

# Assembly Instructions

### Hardware
* Using the M2 screws, attach the NoIR Camera on the underside of the VeinCam hat. 
* Plug the flat flex cable into the camera connector on the Raspberry Pi.
* Connect the VeinCam hat to the Raspberry Pi, ensuring that the flat flex cable does not get pinched. The cable routing is not ideal, but it will all fit inbetween the two boards. 
* Follow the [Software](#Software) instructions to get the board up and running. This is required before continuing assembly as the cameras focus cannot be changed after assembly.
* Using the cross shaped cutout on the VeinCam back panel, adjust the focus ring on the camera until objects 20-30cm away from the lens are in focus. It may be required to use pliers or tweezers to initially move the focus ring, however once it is loose the provided tool can be used. 
* Insert the IR filter into the small cutout on the front acrylic panel. It will only go in from the back side of the acrylic, so if it does not fit try flipping the parts around until they fit. 
* Place the M2.5 screws through the front panel and place on the table top down. Slide 3mm spacers over the screws, one per screw.
* Position the 11mm spacers between the VeinCam hat and the Raspberry PI. Locate the holes in the VeinCam hat over the M2.5 screws and slide into position. May require moving the 11mm spacers until they line up with the holes. 
* Place the remaining 3mm spacers on top of the Raspberry Pi. Install the rear acrylic with the SD card cutout located over the SD card, and install the M2.5 nuts. Using a phillips head screwdriver tighted the screws until snug. 
* Congratulations, you can now look at your veins!    

### Software

#### Connecting to the pi

* Apply power to the raspberry pi through the USB power port
* Wait for the pi to boot, indicated by the 'ready' LED
* Connect to the pi's wifi network on the chosen device
* Connect to the VeinCam server through a web browser on the chosen device
* Press the 'on' switch to activate the camera  

#### Changing the user parameters 

* To change the base URL: 
    - Change the `10.0.0.5` variable in the autohotspot launch script

* To change the wifi name:
    - ssh into the pi 
    - Run: `cd /etc/`
    - Run: `nano hostname`
    - Change the host name
    - When finished press `ctrl + x`, `Y`, `Enter`

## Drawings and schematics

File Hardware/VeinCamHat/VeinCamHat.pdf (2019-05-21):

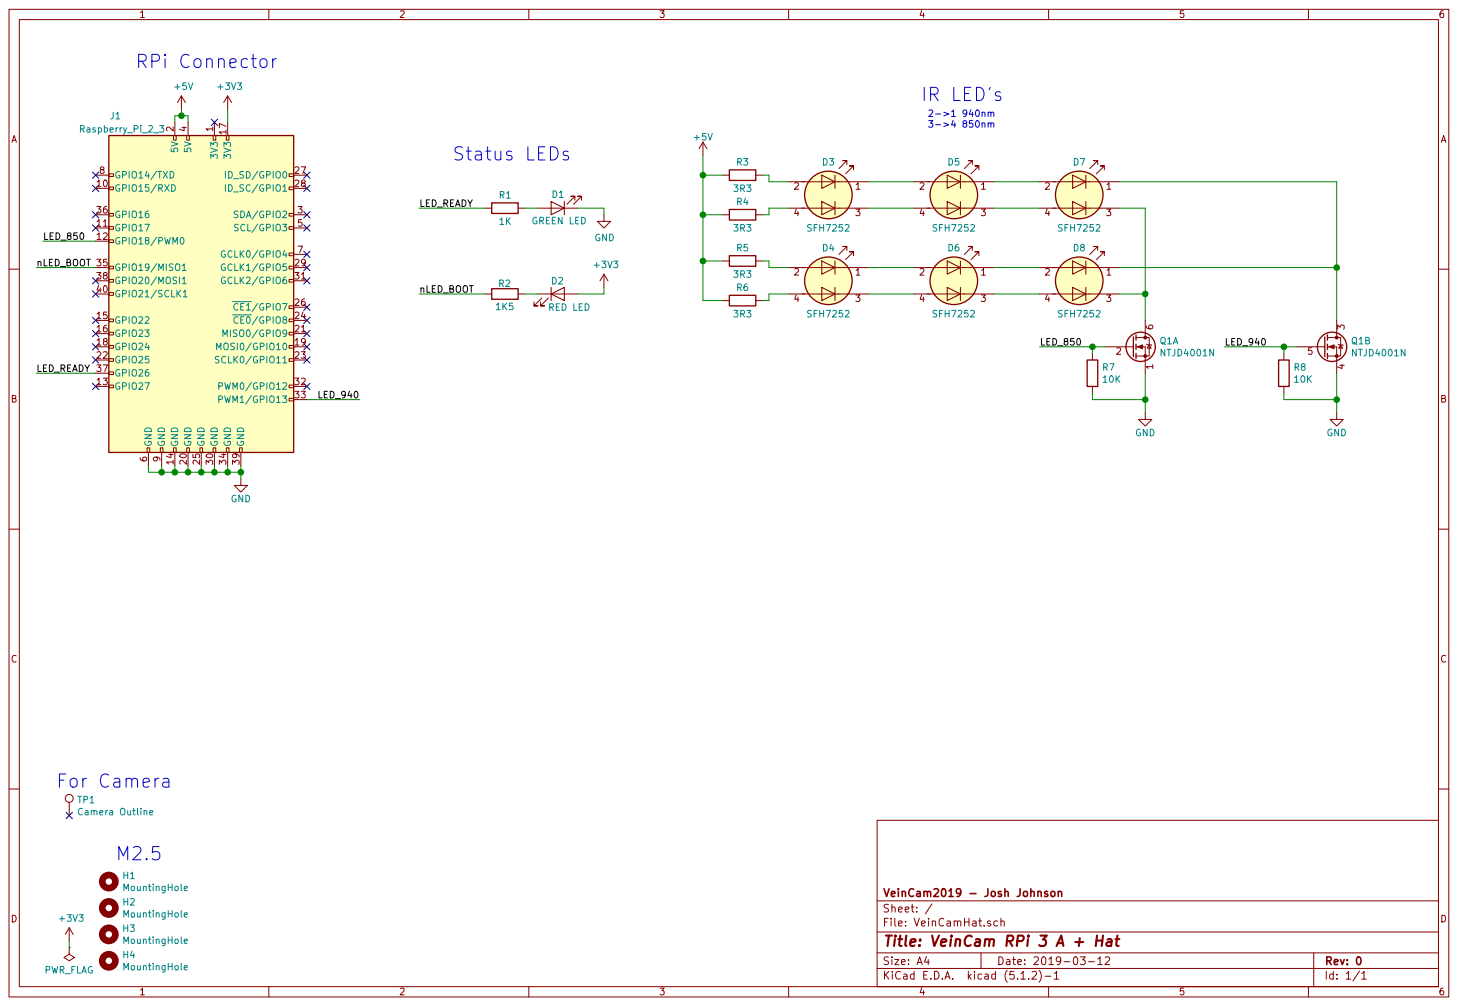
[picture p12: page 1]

Id: 1/1 Title: VeinCam RPi 3 A + Hat File: VeinCamHat.sch Sheet: / VeinCam2019 - Josh Johnson RPi Connector

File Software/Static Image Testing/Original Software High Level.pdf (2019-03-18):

## app.py

1 | 1

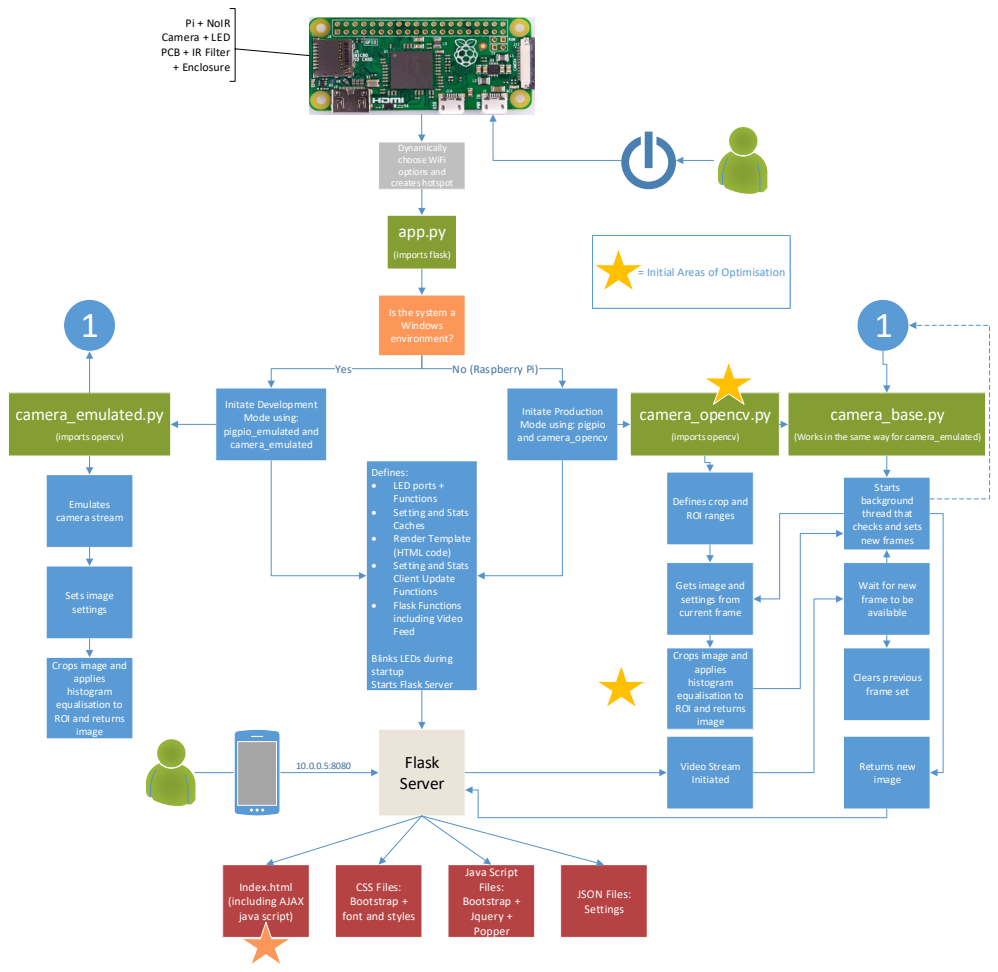
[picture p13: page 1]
Initate Development Mode using: pigpio_emulated and camera_emulated; Yes; Dynamically choose WiFi options and creates hotspot; (imports flask); camera_opencv.py; (imports opencv); camera_emulated.py; Index.html (including AJAX java script); Java Script Files: Bootstrap + Jquery + Popper; JSON Files: Settings; Flask Server; camera_base.py; Video Stream Initiated; Emulates camera stream; Clears previous frame set; Returns new image; Sets image settings

Pi + NoIR
Camera + LED
PCB + IR Filter
+ Enclosure

= Initial Areas of Optimisation

Is the system a
Windows
environment?

No (Raspberry Pi)

Initate Production
Mode using: pigpio
and camera_opencv

(Works in the same way for camera_emulated)

Defines:
• LED ports +
Functions
• Setting and Stats
Caches
• Render Template
(HTML code)
Client Update
• Flask Functions
including Video
Feed

Starts
background
thread that
checks and sets
new frames

Defines crop and
ROI ranges

Gets image and
settings from
current frame

Wait for new
frame to be
available

Blinks LEDs during
startup
Starts Flask Server

Crops image and
applies
histogram
equalisation to
ROI and returns
image

CSS Files:
Bootstrap +
font and styles

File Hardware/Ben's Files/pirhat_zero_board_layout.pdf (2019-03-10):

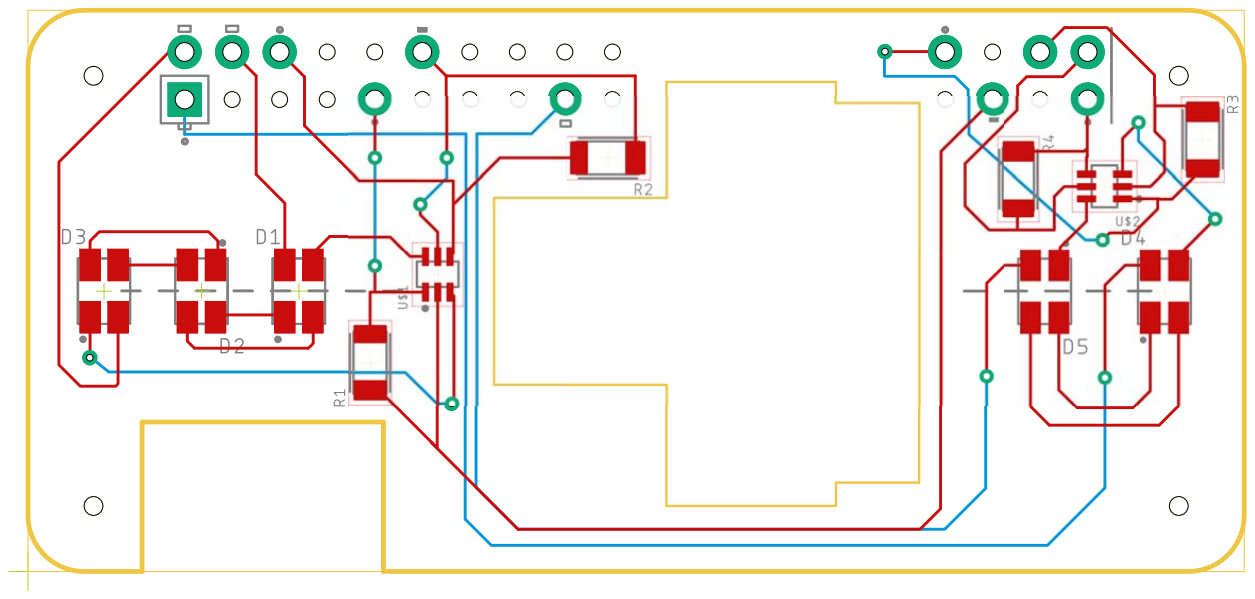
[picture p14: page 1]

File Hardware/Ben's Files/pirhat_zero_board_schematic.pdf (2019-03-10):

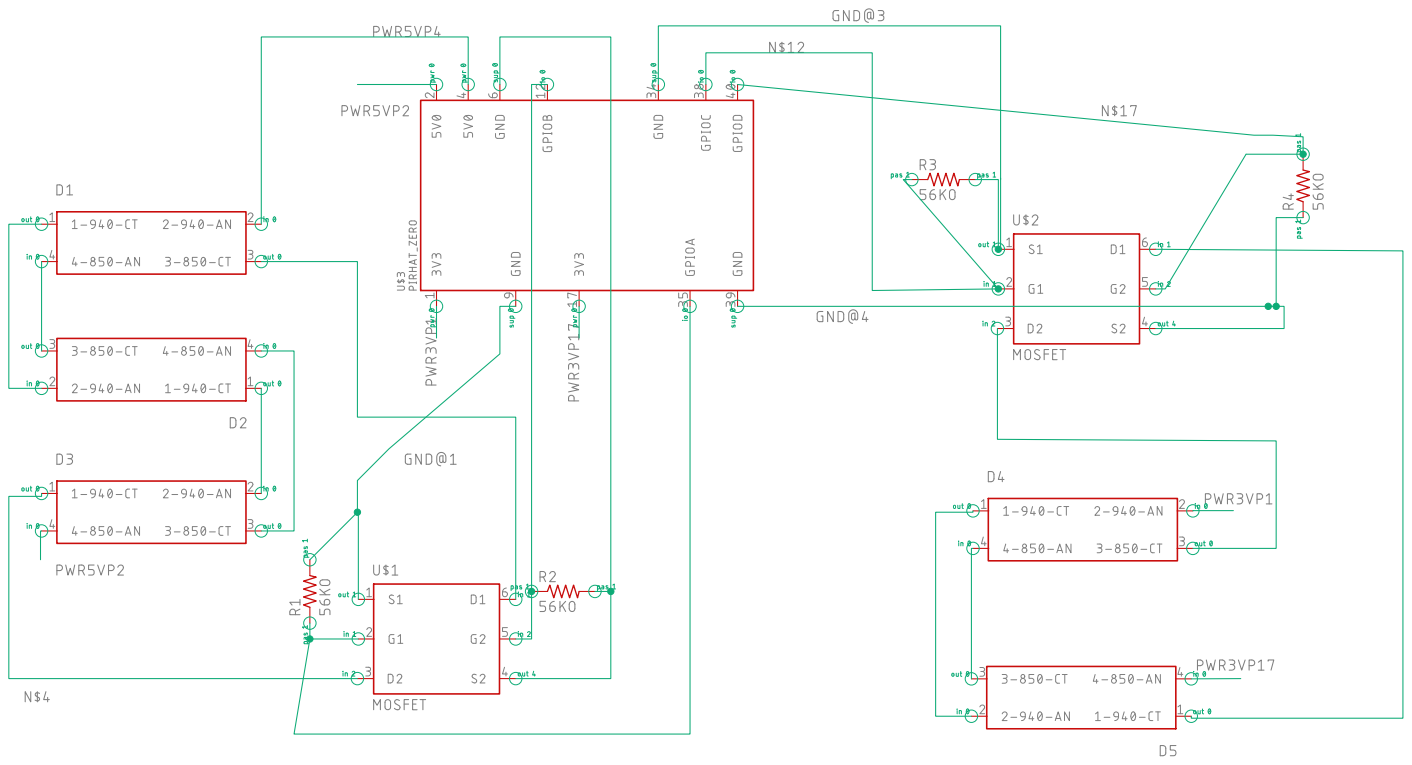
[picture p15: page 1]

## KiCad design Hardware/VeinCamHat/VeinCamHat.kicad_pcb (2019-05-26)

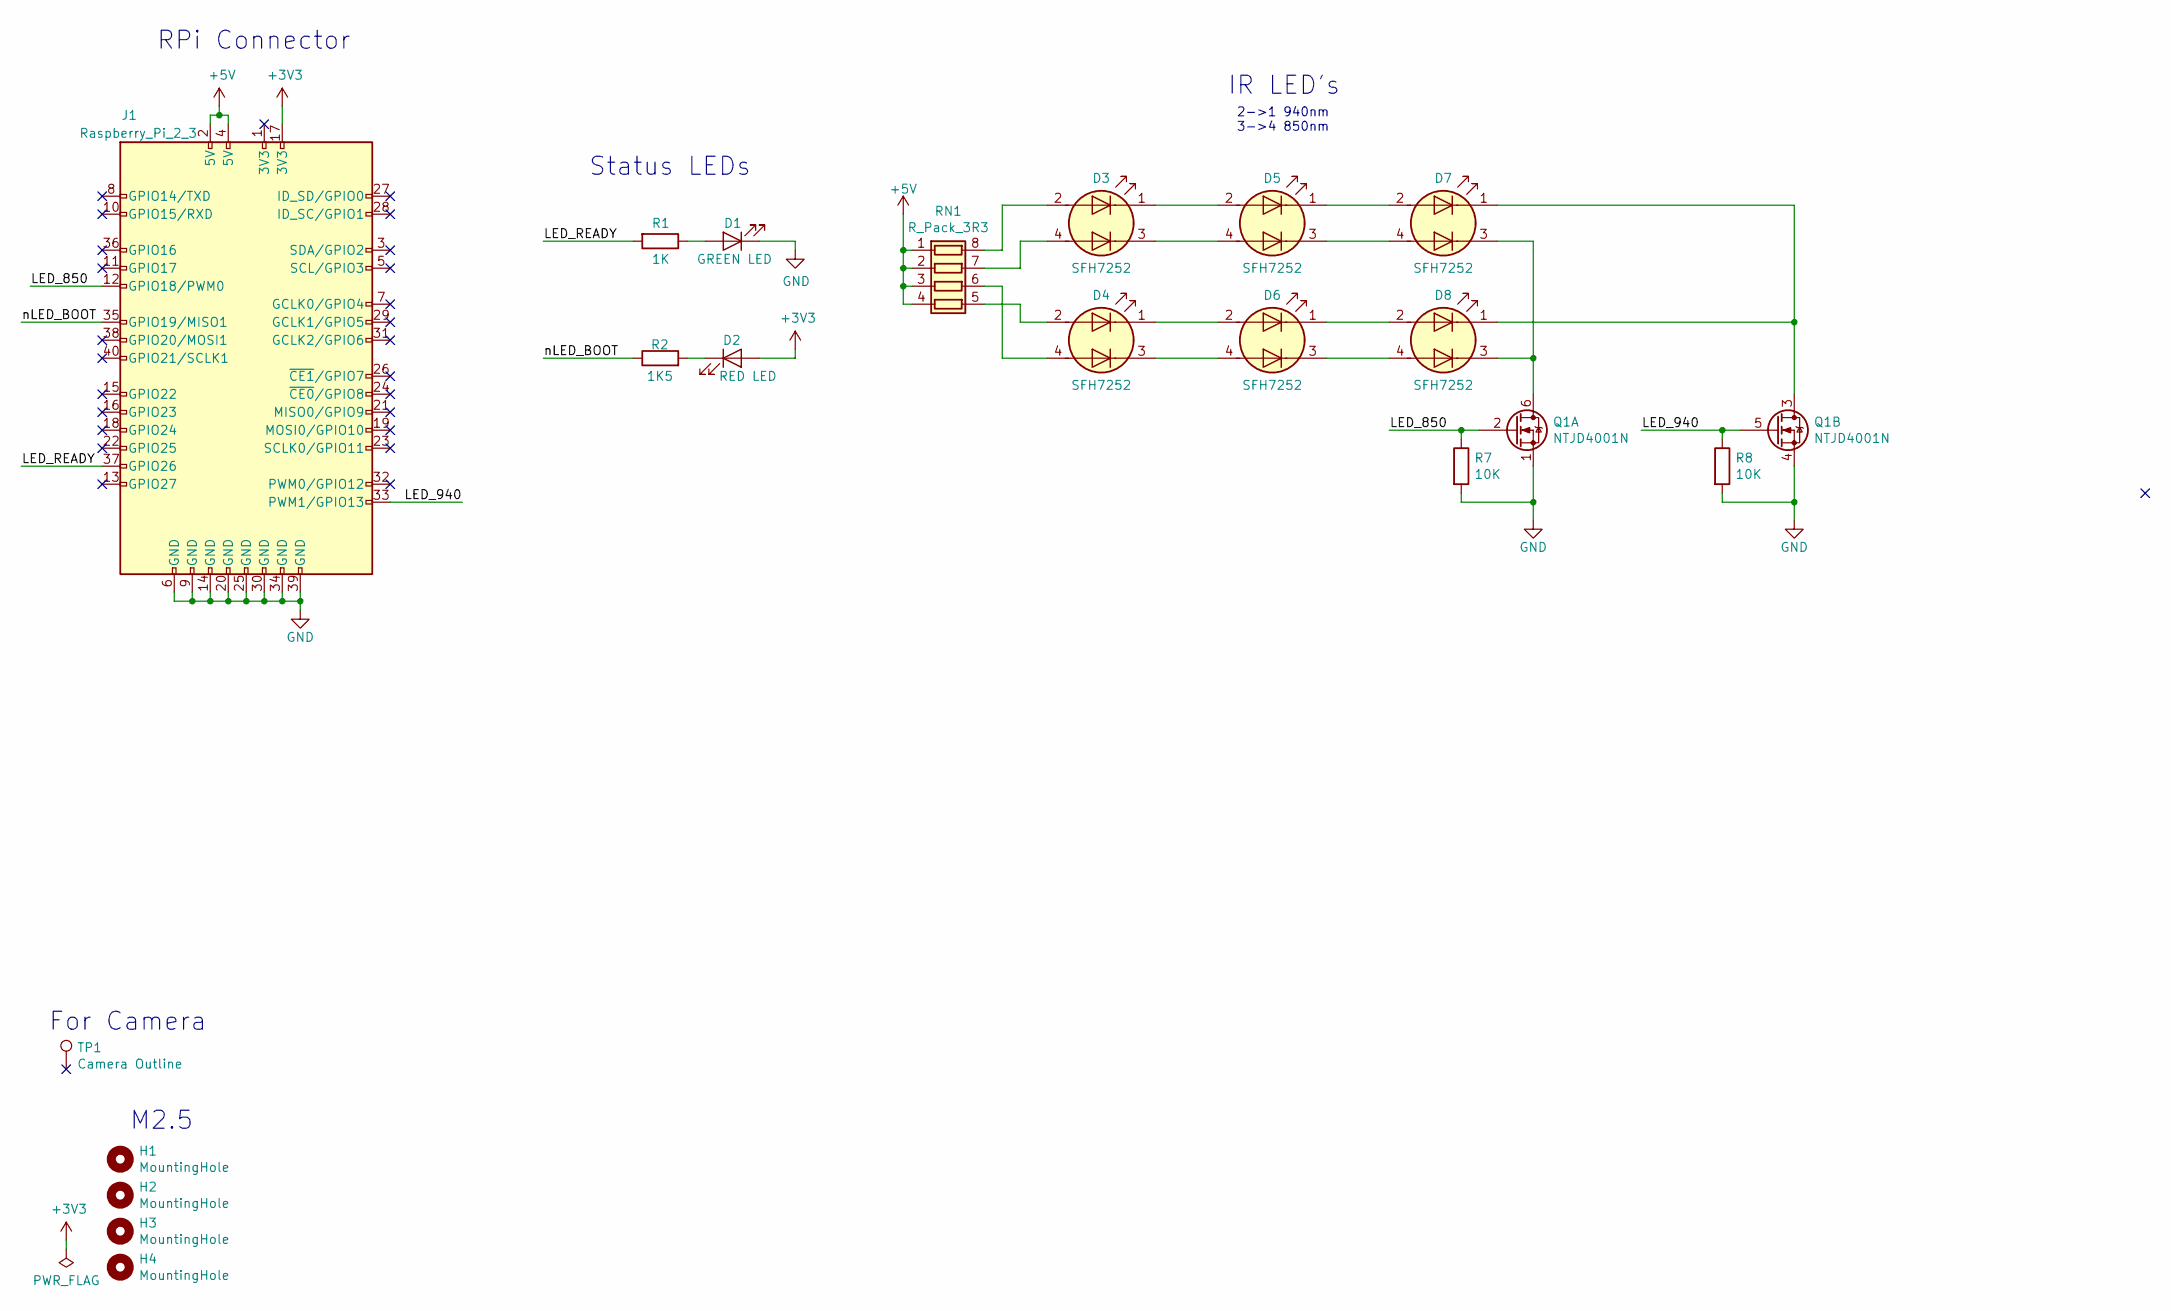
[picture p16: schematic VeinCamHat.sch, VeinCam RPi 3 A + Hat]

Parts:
D1: GREEN LED; LED_0805_2012Metric
D2: RED LED; LED_0805_2012Metric
D3, D4, D5, D6, D7, D8: SFH7252
H1, H2, H3, H4: MountingHole; MountingHole_2.7mm_M2.5
J1: Raspberry_Pi_2_3; PinSocket_2x20_P2.54mm_Vertical
Q1: NTJD4001N; SOT-363_SC-70-6
R1: 1K; R_0603_1608Metric
R2: 1K5; R_0603_1608Metric
R7, R8: 10K; R_0603_1608Metric
RN1: R_Pack_3R3; R_Array_Convex_4x0603
TP1: Camera Outline; PiCamera

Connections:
+3V3: D2.2 (A), J1.17 (3V3)
+5V: J1.2 (5V), J1.4 (5V), RN1.1 (R1.1), RN1.2 (R2.1), RN1.3 (R3.1), RN1.4 (R4.1)
/LED_850: J1.12 (GPIO18/PWM0), Q1.2 (G), R7.1
/LED_940: J1.33 (PWM1/GPIO13), Q1.5 (G), R8.1
/LED_READY: J1.37 (GPIO26), R1.2
/nLED_BOOT: J1.35 (GPIO19/MISO1), R2.1
GND: D1.1 (K), J1.6 (GND), J1.9 (GND), J1.14 (GND), J1.20 (GND), J1.25 (GND), J1.30 (GND), J1.34 (GND), J1.39 (GND), Q1.1 (S), Q1.4 (S), R7.2, R8.2
unnamed: D1.2 (A), R1.1
unnamed: D2.1 (K), R2.2
unnamed: D3.1 (K2), D5.2 (A2)
unnamed: D3.2 (A2), RN1.8 (R1.2)
unnamed: D3.3 (K1), D5.4 (A1)
unnamed: D3.4 (A1), RN1.7 (R2.2)
unnamed: D4.1 (K2), D6.2 (A2)
unnamed: D4.2 (A2), RN1.5 (R4.2)
unnamed: D4.3 (K1), D6.4 (A1)
unnamed: D4.4 (A1), RN1.6 (R3.2)
unnamed: D5.1 (K2), D7.2 (A2)
unnamed: D5.3 (K1), D7.4 (A1)
unnamed: D6.1 (K2), D8.2 (A2)
unnamed: D6.3 (K1), D8.4 (A1)
unnamed: D7.1 (K2), D8.1 (K2), Q1.3 (D)
unnamed: D7.3 (K1), D8.3 (K1), Q1.6 (D)

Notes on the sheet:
RPi Connector
M2.5
IR LED's
2->1 940nm 3->4 850nm
Status LEDs
For Camera

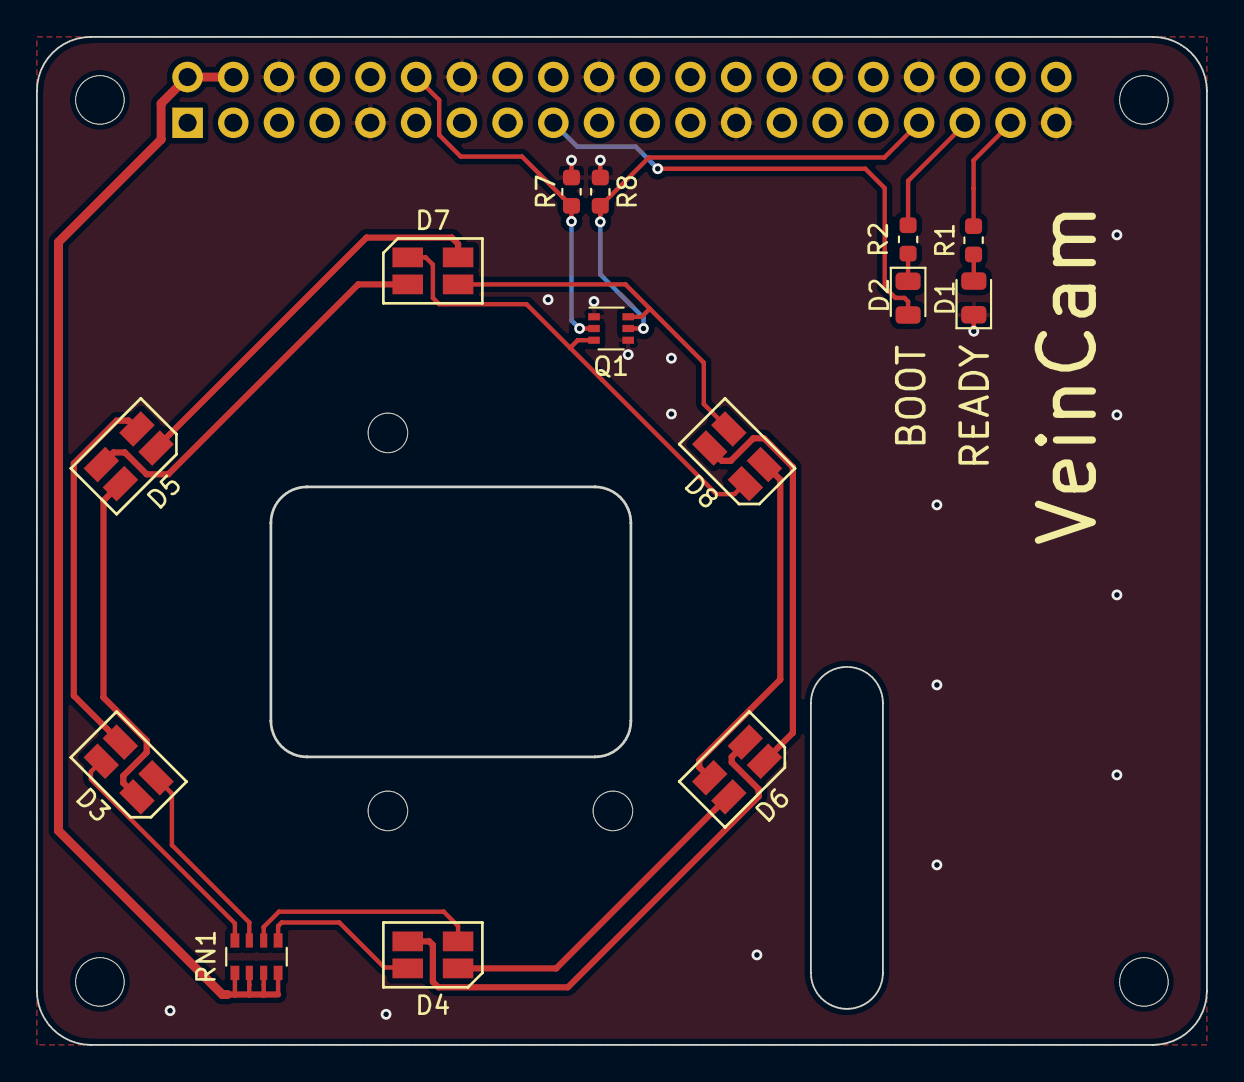
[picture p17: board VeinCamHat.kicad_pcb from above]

Board: 2 copper layers, 65.0 x 56.0 mm, 20 parts (1 on the bottom side), 23 nets.

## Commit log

2019-03-12 Added VeinCamHat PCA files
    [VeinCamHat.kicad_pcb, VeinCamHat.sch]
2019-03-13 Hardware Updates
    [VeinCamHat.sch]
2019-03-13 Schematic for RPiZero hat completed, BOM generation and Estimated Financials completed.
    [Estimated Financials.xlsx, VeinCamHat.sch, VeinCamHatZero.kicad_pcb, VeinCamHatZero.sch]
2019-03-13 fix typo in financials + add missing kicad files
    [Estimated Financials.xlsx]
2019-03-14 Added SBC Comparison
    [SBC Comparison.xlsx]
2019-03-18 Laid out VeinCamHatZero and added IR LED footprint/model
    [VeinCamHatZero.kicad_pcb, VeinCamHatZero.sch]
2019-03-18 Added footprints for VeinCamHat and begun layout
    [VeinCamHat.kicad_pcb, VeinCamHat.sch, VeinCamHatZero.kicad_pcb]
2019-03-18 Changes to renders
    [Estimated Financials.xlsx, VeinCamHatZero.kicad_pcb]
2019-03-19 Changed plans for VeinCam Plus, both boards laid out
    [Estimated Financials.xlsx, VeinCamHat.csv, VeinCamHat.kicad_pcb, VeinCamHat.sch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]
2019-03-19 More Hardware changes, both boards complete
    [Estimated Financials.xlsx, VeinCamHat.kicad_pcb, VeinCamHat.sch, VeinCamHatZero.kicad_pcb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]
2019-03-19 updates to renders
    [Estimated Financials.xlsx]
2019-03-22 final board changes, gerbers generated
    [VeinCamHat-B.Cu.gbl, VeinCamHat-B.Mask.gbs, VeinCamHat-B.SilkS.gbo, VeinCamHat-Cmts.User.gbr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]
2019-03-22 Finished boards, v0.2 gerbers zipped and sent off to fab
    [VeinCamHat-B.Cu.gbl, VeinCamHat-B.SilkS.gbo, VeinCamHat-B_Cu.gbl, VeinCamHat-B_Mask.gbs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]
2019-03-23 found possible IR filter suppliers
    [Estimated Financials.xlsx]
2019-03-23 added potential suppliers for IR filter
    [Estimated Financials.xlsx]
2019-03-28 Added 3d Models + hardware readme
    [Estimated Financials.xlsx]
2019-03-29 DXF's and STL's for cutting and printing generated
    [11mm M3 Spacer v3.stl, 2.5mm M3 Spacer v5.stl, Acrylic Bottom.stl, Acrylic Top.stl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]
2019-04-01 Updated case design and spacers
    [3mm M3 Spacer v5.stl]
2019-04-02 Changed pricing details and added links for mounting hardware.
    [Estimated Financials.xlsx]
2019-04-07 changed logo direction on veincam, added licencing document
    [VeinCamHat.kicad_pcb]
2019-04-08 Added v2 of the VeinCam Zero board
    [VeinCamHatZero-B_Cu.gbl, VeinCamHatZero-B_Mask.gbs, VeinCamHatZero-B_SilkS.gbo, VeinCamHatZero-Cmts_User.gbr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]
2019-04-11 VC zero changes
    [VeinCamHatZero.kicad_pcb]
2019-04-19 More schematic / PCB changes
    [11mm M3 Spacer v3.stl, 2.5mm M3 Spacer v5.stl, 3mm M3 Spacer v5.stl, Acrylic Bottom.stl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]
2019-04-19 updated schematic
    [VeinCamHat.sch]
2019-04-23 Josh can't read datasheets correctly
    [VeinCamHat.sch]
2019-04-23 piopencv big cleanup into 1 file + app.py fixes LED pins fixed in app.py included launch file with new boot LED write
2019-04-24 quick syntax fix camera_piopencv
2019-04-29 Client feedback for device assembly and testing
2019-04-30 Software Diary update to current (30.04.2019)
2019-04-30 Added DXFs of acrylic plates
    [VeinCamHatZero-B_Cu.gbl, VeinCamHatZero-B_Mask.gbs, VeinCamHatZero-B_SilkS.gbo, VeinCamHatZero-Cmts_User.gbr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]
2019-05-12 Added Assembly Instructions and updated pricing
    [Estimated Financials.xlsx]
2019-05-20 updating hardware things
    [Estimated Financials.xlsx, VeinCamHat-B_Cu.gbr, VeinCamHat-B_Mask.gbr, VeinCamHat-B_SilkS.gbr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]
2019-05-21 Added software assembly instructions
2019-05-26 Updates to board and generation of final production outputs
    [BOM_MECH.xlsx, BOM_PCB.xlsx, VeinCamHat.csv, VeinCamHat.kicad_pcb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]
